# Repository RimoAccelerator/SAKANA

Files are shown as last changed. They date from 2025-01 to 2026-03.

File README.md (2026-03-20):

**非常重要提醒：20260320版本进行了重大更新，修正了在扫速控制和曲线显示方面的bug，包括固件和Controller，请务必更新。从旧版本更新过来的用户，请到Advance里，点击Reset，将预置的校正参数清除！**

**VERY Important Notice:** The 20260320 version includes major updates that fix bugs related to scan rate control and curve display. This update applies to both the firmware and the Controller—please make sure to update.

For users upgrading from older versions, go to **Advance**, click **Reset**, and clear the preset calibration parameters.

[中文](#cn) | [English](#en)

# SAKANA：年轻人第一台循环伏安的全面制造指南

SAKANA是一款基于树莓派Pico的电化学工作站，其中包含了所有软硬件信息。这篇介绍将从第一视角呈现SAKANA的开发和探索过程，以便读者透彻了解仪器的设计思想。

目录结构：

- **Hardware**
  
  Gerber_SAKANA_PCB.zip： PCB制板文件
  
  SAKANA_PCB.epro：PCB设计文件（基于立创EDA）
  
  Shell.zip：外壳模型，可进行3D打印

- **Sources**
  
  main.py：Pico上的Micropython文件

- **sources_SakanaController**
  
  上位机控制软件源代码，Releases中有编译后的可执行文件

鉴于绝大多数化学工作者都像我一样，没有接受过系统的电子工程教育，本文中会详细介绍电路的设计过程。如果你有此类基础，可直接跳转到**6. 建立连接**。

**1. 背景介绍**

   现代电化学工作站基于运算放大器（简称运放）进行设计，主要在20世纪70年代发展起来。早年文献中对电化学工作站的设计原则、特别是电路稳定性问题进行了诸多讨论，这些讨论对电路知识有较高的要求，有兴趣的读者可以自行查阅。近十多年来，得益于单片机技术的普及，使用以Arduino为代表的单片机控制从而低成本制造电化学工作站的案例不断见诸报道，以至于到了相当丰富的程度。甚至已经有学校将自制电化学工作站纳入了分析化学实验课程中（https://www.chem.uci.edu/~unicorn/243/labs/W2019Chem243Lab3.pdf）。

   

   本文的设计原型来自2016年Meloni的工作（J. Chem. Educ. 2016, 93, 7, 1320–1322）。Meloni报道了基于Arduino的电化学工作站设计，并给出了电路图和简易源代码。然而不幸的是，虽然Meloni文中呈现了良好的结果，但如果直接照搬它的设计，仔细考察，就会发现其实并不能用。接下来我们会展示这一电路的原理、以及本文的装置的设计和改进过程。

**2. Meloni原型机的原理**

   用于循环伏安的电化学工作站基于三电极系统。对三电极系统的理解是仪器分析课程的基本内容，本文不再赘述。一个合格的电化学工作站需要确保以下几点：

   a. 在参比电极(RE)上没有电流流过；

   b. 能精确控制工作电极（WE）相对于RE的电位，并且这一电位需要以最高几个Hz的频率变化；

   c. 能精确测量通过WE的电流，电流的量级在零点几到几百uA之间。

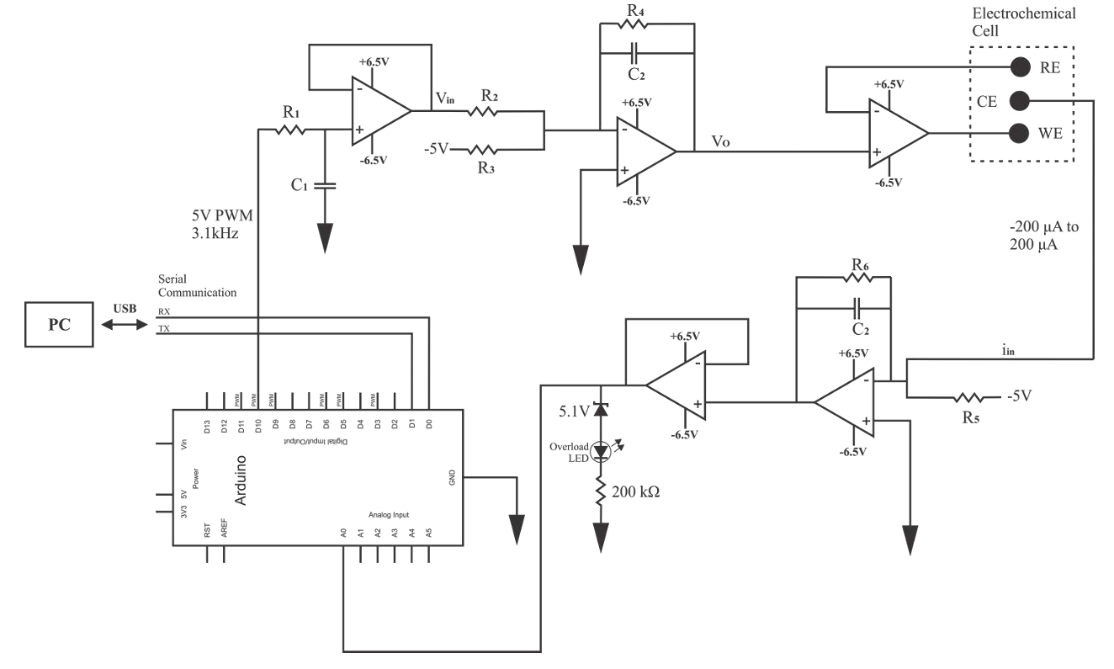
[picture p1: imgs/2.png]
   

a. 电压控制电路  

运放是现代电化学工作站的核心，要理解电压控制电路必须首先理解运放。

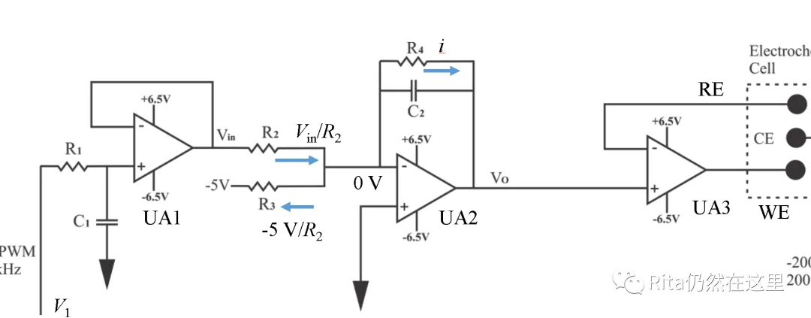
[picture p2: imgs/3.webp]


一个运放至少有5个引脚：2个电源引脚（图中正负6.5 V），一个同相输入端（图中+），一个反相输入端（图中-），一个输出端。当输出端与反相输入端通过电阻连接时，构成了负反馈电路；对于理想运放，输入端可视为无穷大的电阻，而一旦构成负反馈，则两个输入端电位相等且都没有电流流过。因此对于上图中左侧的运放，输出电压Vin始终等于同相输入端电位，这被称为跟随器，可对电路起到隔离作用。接下来为了解出第二个运放的输出电位Vo，可设通过R4的电流为i，则Vo = -iR4，可知运放对电流有放大作用，放大倍数取决于反馈电阻。由于通过反相输入端的电流为0，可知i = Vin / R2 - 5 V / R2，进而可求出Vo。通过控制Vin = V1，即可控制Vo；随后Vo接到UA3上，只要RE和CE放在电解池中，就再次构成负反馈，RE上的电压即等于V1。  

之所以要采用这样的设计，是由于多数单片机只能输出正电压，因此需要通过R3施加一个负电压偏置来将其转换为循环伏安所需要的电压范围。在Meloni原型机中，V1通过Arduino的PWM供给。PWM是通过让输出信号在0 V和（对于Arduino来说）5 V间快速切换产生方波的技术，假设占空比为a，则等效输出5 V * a的电压。为了将这种方波信号转换为循环伏安所需要的直流信号，Meloni原型机在R1和UA1之间对地接入电容C1，从而构成了RC滤波电路。RC滤波电路对电信号的阻抗随频率上升而快速增加，对于频率大于1/(2pi*RC)的信号，通过RC滤波器后衰减大于3 dB，这被称为截止频率。方波信号经过傅里叶展开后，可视为直流信号叠加一系列高频信号；理想上，当高频信号被充分滤除，就可以得到5 V * a的直流电压。随后经过UA1~UA3，最终反映到RE对地的电位上。

类似地，UA2上的C2同样与R4构成RC滤波器，从而尽可能滤除运放带来的噪声。

b. 电流采样电路

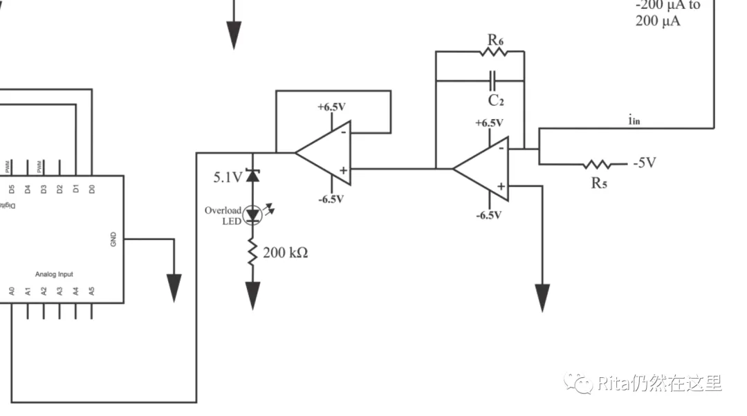
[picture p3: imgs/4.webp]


Meloni原型机中，电流采样电路接在CE上，通过R5施加5 V的偏置，接到运放上，通过R6负反馈，使得CE的电位恒为0。两者混合后的电流i被放大为电位iR6（恒为正，同样是由于单片机只能读取正电位），经过一个跟随器后进入Arduino的ADC引脚（Analog to Digital）从而被读取。读完上文后，相信读者已经会计算通过CE的电流与ADC读数的关系了。

你发现了什么不对了吗？

在Meloni原型机中，CE和WE的位置画反了。我们并不关心CE上的电位是多少，而必须控制WE和RE的电位差，因此必须将WE接在电流采集电路处，从而使得上面控制的RE相对于地的电位等同于WE相对于RE的电位的负值。  

总之，现在你已经理解了Meloni原型机的原理，接下来就开始实现吧。

**3. 材料清单**

- 

- | 名称               | 数量              | 链接                                                 | 备注      |
  | ---------------- | --------------- | -------------------------------------------------- | ------- |
  | 树莓派Pico          | 1               |                                                    |         |
  | MCP4725模块        | 1               | https://item.taobao.com/item.htm?&id=549632416001  |         |
  | ADS1115模块        | 1               | https://item.taobao.com/item.htm?&id=631122402654  |         |
  | INA219芯片         | 1               | https://item.taobao.com/item.htm?id=725297963549   |         |
  | 6 V输出DC/DC升压模块   | 1               | https://item.taobao.com/item.htm?id=666072862041   |         |
  | OP297运放          | 2               | https://item.taobao.com/item.htm?id=599390292581   |         |
  | 继电器模块            | 4（v1.0）或3（v2.0） | https://item.taobao.com/item.htm?&id=628701168992  |         |
  | CH340串口模块        | 1               | https://detail.tmall.com/item.htm?id=41323941056   |         |
  | GM12043AKCZ-R7   | 1               | https://item.szlcsc.com/8421183.html               | 仅v2.0需要 |
  | GM1206AUJZ-R7    | 1               | https://item.szlcsc.com/50919536.html              | 仅v2.0需要 |
  | 共模扼流圈ACM9070-272 | 1               | https://item.taobao.com/item.htm?id=711722477029   | 仅v2.0需要 |
  | 电容：10 uF         | 2               |                                                    |         |
  | 电容：2.2 uF        | 2               |                                                    | 仅v2.0需要 |
  | 电容：0.1 uF        | 10              |                                                    |         |
  | 电容：1 uF          | 3               |                                                    |         |
  | 电容：68 nF         | 1               |                                                    |         |
  | 电阻：4k7           | 4               |                                                    |         |
  | 电阻：10k           | 5               |                                                    |         |
  | 电阻：6k8           | 2               |                                                    |         |
  | 电阻：68k           | 1               |                                                    | 仅v1.0需要 |
  | 电阻：680k          | 1               |                                                    |         |
  | 电阻：1k            | 1               |                                                    |         |
  | 电阻：15k           | 2               |                                                    | 仅v2.0需要 |
  | GX16航空插座弯头       | 1               | https://item.taobao.com/item.htm?id=890416759846   | 仅v2.0需要 |
  | 屏蔽线母头GX16-4芯     | 1               | https://detail.tmall.com/item.htm?&id=691474825406 | 仅v2.0需要 |
  
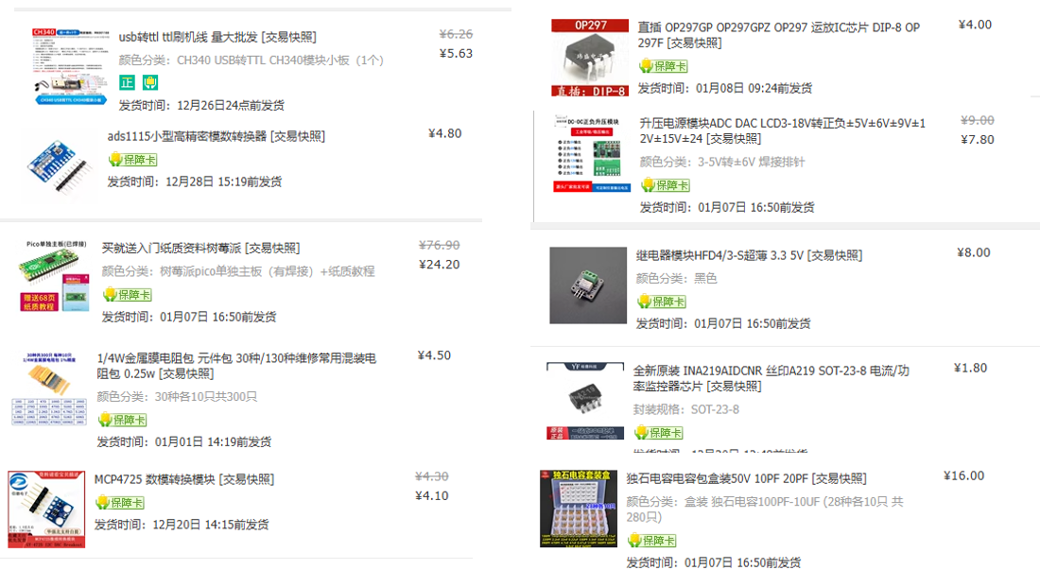
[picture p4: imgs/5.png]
  
  
  （没有任何淘宝店铺赞助本文）

Meloni使用了Arduino，而本文使用树莓派Pico。Pico的性能更为优异，而价格却更加低廉。值得注意的是Pico的输出电压是3.3 V（另有一个5 V引脚），因此基于输出5 V的Arduino的电路中元件取值要重新换算。  

**4. Meloni原型机的实现和失败，与第一版可工作的电路**  

Meloni已经给出了完整的电路图，将其实现是十分简单的事情，不再赘述。唯一值得一提的是，电路中需要使用负电压，仅使用Pico无法做到，本文中使用了升压电源模块得到正负6 V。正电压非常标准，而负电压实际大约为-5.5 V。它同样用于给运放供电。绝大多数运放的输出电压都位于两个电源引脚的电压之间，通常是一个较窄的范围（这将成为日后电阻选值的考量），选择轨到轨运放可以输出到接近供电电压的范围。

然而很快就会发现，这套电路的立足之本，即通过对PWM滤波以控制RE上的电位的做法完全不可行。一方面，即使经过滤波，电压仍然会不可避免地波动（纹波现象），而另一方面的问题则更加严重：

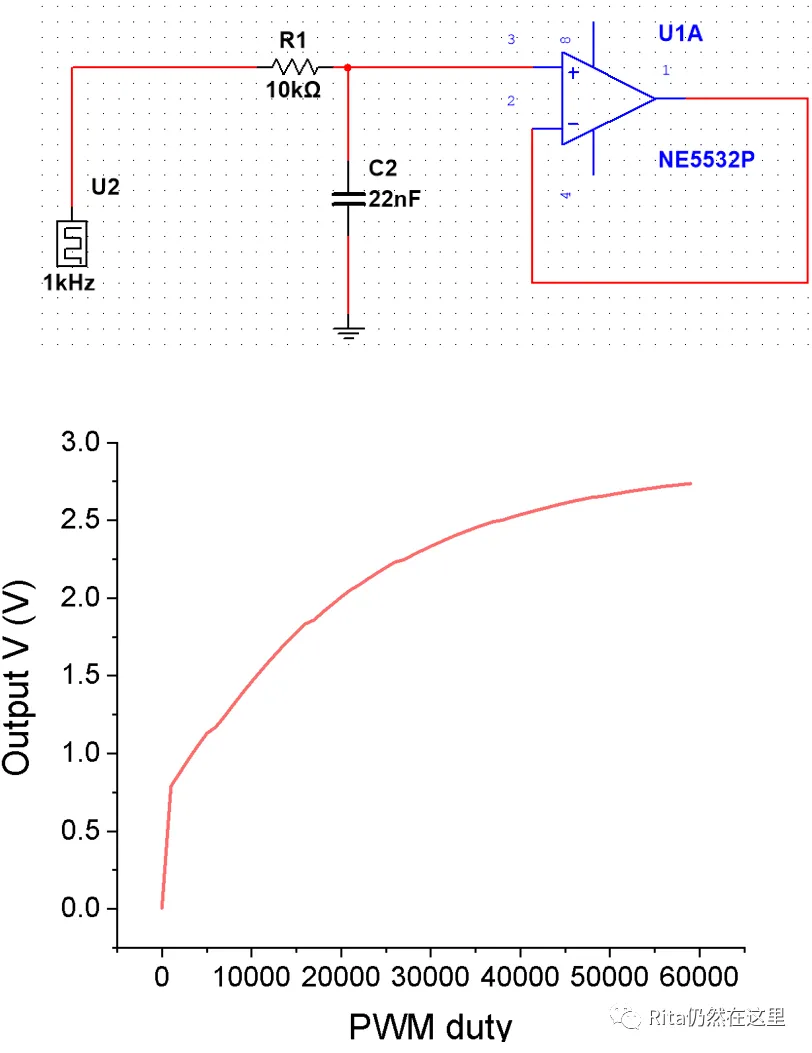
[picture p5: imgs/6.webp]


上图展示了PWM占空比与经过滤波得到的电压的关系。理想情况下，电压应随占空比呈现线性，但事实完全不同，呈现出一条十分不规则的曲线。这种情况下，通过PWM控制RE上的电压完全不可靠！  

幸运的是，由于现代电子工业高度发达，许多电路中的功能可以方便地找到模块，像搭积木一样处理。事实上，如果想输出可调的电压，并不需要手动设计电源电路，使用（3）中展示的MCP4725模块即可。它基于I2C协议和Pico连接，可以方便地使用Github上现成的库进行控制。经过实测，它可以精确、稳定地输出0 ~ 4.5 V的直流电压。

图片

使用MCP4725后，采用了如上电路以适配Pico的性能。在面包板上搭建好后，已经可以用于测定盐水中的赤血盐的CV：  

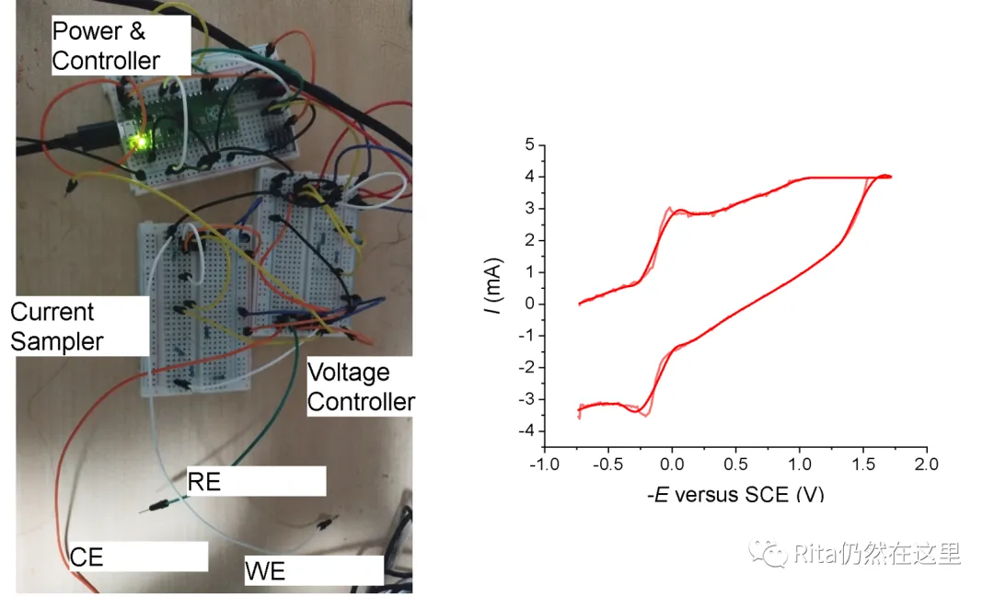
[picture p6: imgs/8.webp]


**5. 进一步改进：重做电流采样**  

上述电路如果作为教学实验，则已经可以了；但如果要用于实际测量，还存在诸多问题。其中最大的问题在于噪声。事实上，Pico ADC的噪声是一个世界性难题，许多人都受此困扰而难以找到解决方案。以下随机展示一个ADC面对直流电的测量结果，可见存在相当程度的不规则的跳变。这一噪声完全来自Pico自身的缺陷，无法被任何外部电路滤除。  

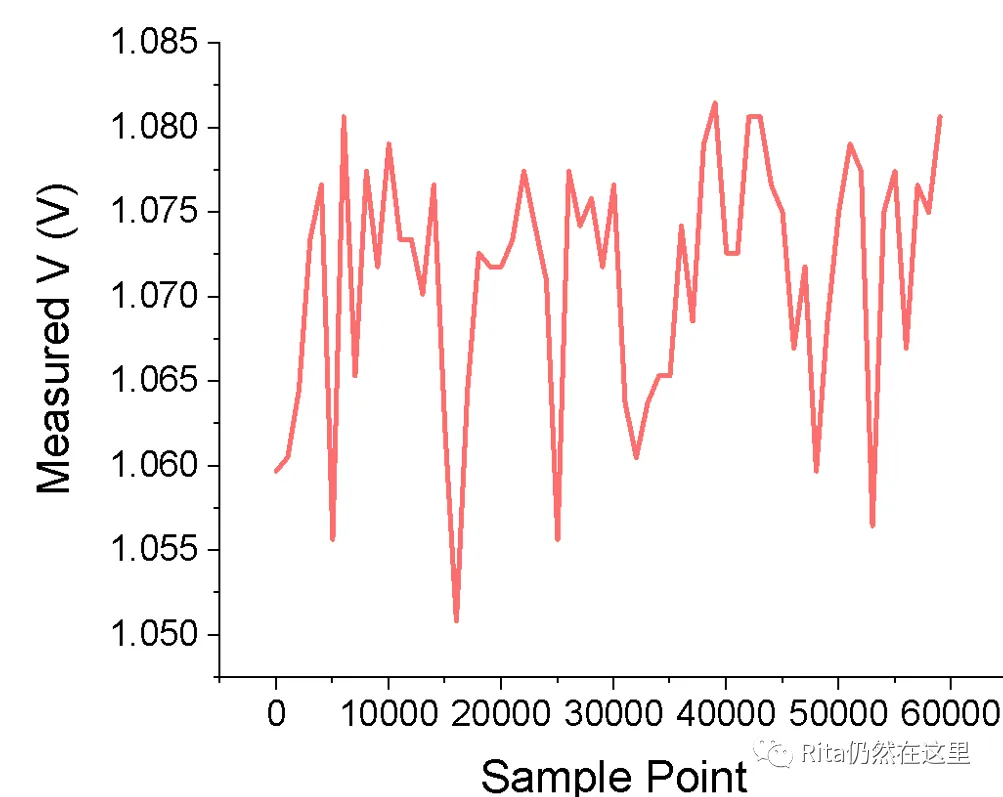
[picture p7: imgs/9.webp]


尽管Pico手册上给出了改进ADC的建议，但最终它们没能起效，因此接下来需要放弃Pico自带的ADC，采用其他模块。在这里，需要用到两个模块：ADS1115电压采集模块，以及INA219电流采集模块。两者都使用I2C协议，和MCP4725共用2根线进行通信。

事实证明，ADS1115的精度良好，可以非常平稳地测定接入的电压，并且可以测定不低于-0.5 V的负压。但问题在于采样频率，ADS1115每秒只能进行860次采样，无法满足CV测试在很短的时间内连续变化电压并进行采样的需求，如果硬上会造成死机。但它可以用于电路的校准：  

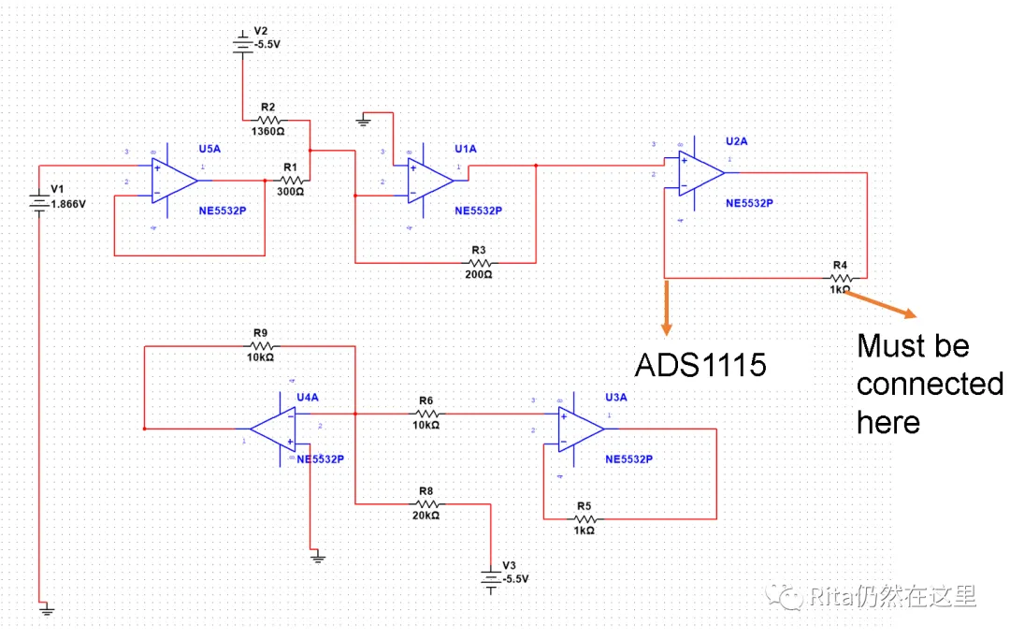
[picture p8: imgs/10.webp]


将RE和CE的接线端连起来（必须这样做，否则无法构成负反馈），用ADS1115测量RE处的电压，即可对仪器进行校准。  

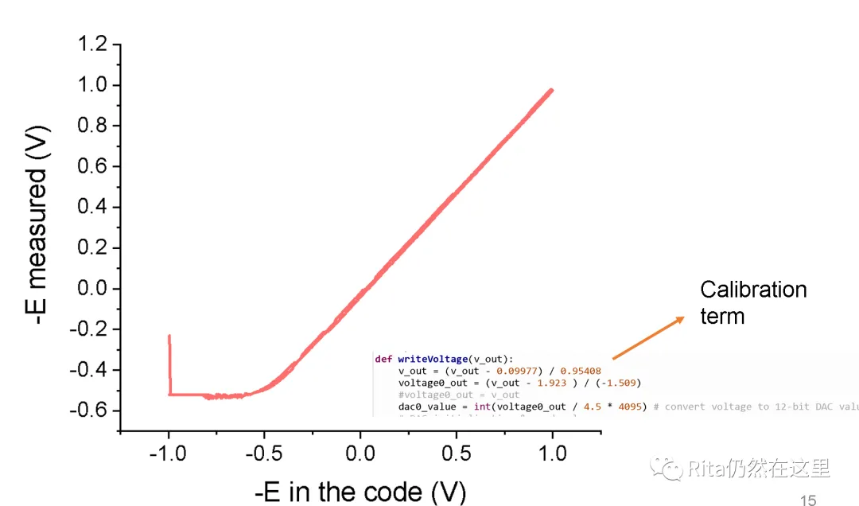
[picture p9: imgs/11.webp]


注意当电压小于-0.5 V时，ADS1115不再能正常工作，而且不仅自己不干活，还会干扰别人，导致RE上的电压异常，因此ADS1115只能用于校准，CV测量时必须同RE断开。

而接下来的INA219将成为电流采样的核心。它与ADC的思路不同，是直接测量电流。INA219本身是个集成电路，需要搭配外围电路使用，商业可得的INA219模块已经集成了一个0.1 Ohm的采样电阻，它通过测定采样电阻上的电压来给出电流，支持正负电流。量程可调，最小量程为400 mA，分辨率为12位，即400/(2^12)~0.1 mA。  

INA219的引入可以使得我们直接去掉电流采样电路冗杂的偏置电压设计，只要将流过WE的电流放大到合适的范围，让INA219采样即可。利用这种思路，在简单尝试后得到了十分积极的初步结果。其中黑线为原始信号，红线为经过平滑后的结果。

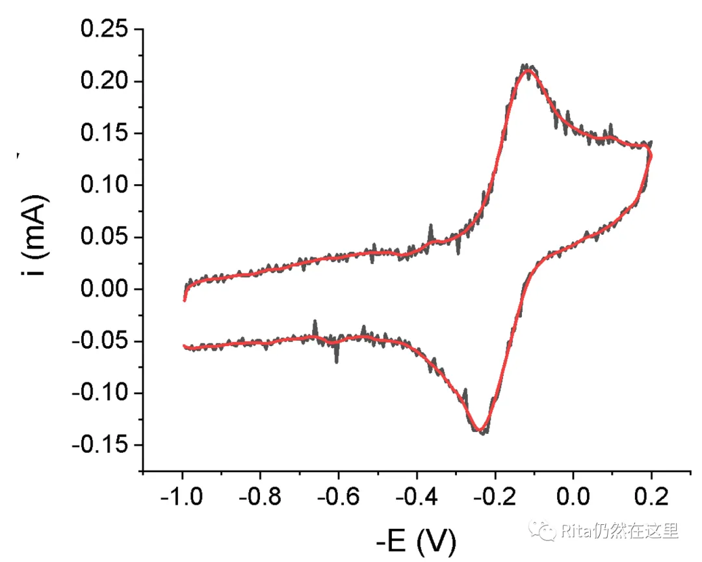
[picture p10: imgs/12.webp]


以下为SAKANA v1.0使用的电路：

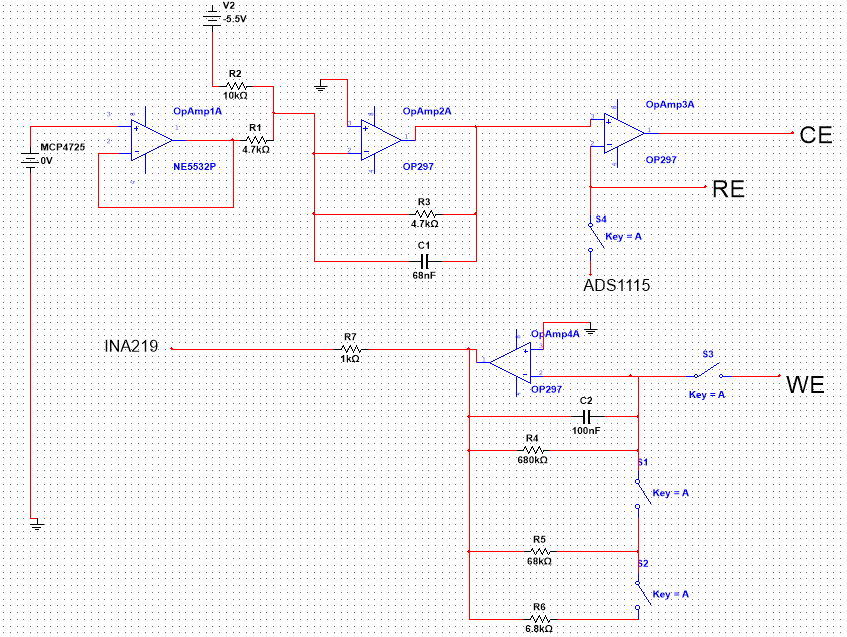
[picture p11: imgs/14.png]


在这一电路中，流过WE的电流i经过一个跨阻放大器，转化为iR的电压信号，其中R可在R4到R6之间选择。经过R7后，通过INA219的实际电流为iR/R7，测量这一电流信号即可换算为流过RE的电流。为了确保INA219的测量精度，iR/R7不能太小，需要在几个mA量级；同时iR又不能太大，必须落在运放能够可靠工作的电压范围内。由于CV波的电流从零点几到几百uA，跨越了3个数量级，采用两个继电器控制接入从6.8 k到680 k之间的电阻以改变量程。

OpAmp2和OpmAmp4的反馈回路上都并联有电容，起到增加运放稳定性和减少输出噪波的作用。借助示波器，可以清晰地看到C1对于确保RE上电压的稳定性有至关重要的作用。没有C1时，RE上的电压会以几百mV的幅度波动：

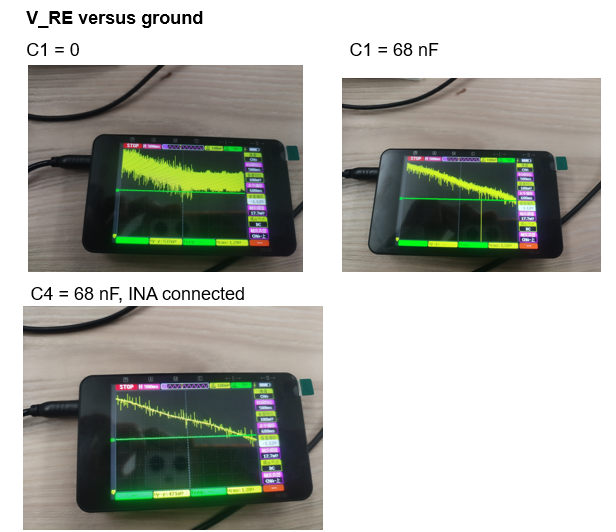
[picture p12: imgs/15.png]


C2同样可以显著抑制噪声。此处经过大量尝试，确定C2取值为100 nF，且不随接入的电阻而变化。较大的C2虽然可以进一步使得输出信号变得平滑，但由于滤除了太多快速变化的信号，导致波形畸变、以及更严重的是当改变设定的输出电压时需要相当长的时间才能达到稳定。

R7是一个1 kOhm的电阻。在设计初期，在R7处曾经使用过更小的电阻，寄希望于它能够使得流过INA219的电流尽可能大，以降低测定误差的影响。但不幸的是，较小的R7会导致测定曲线出现未曾预料的巨幅波动。以下是R7 = 100 Ohm的典型图形：

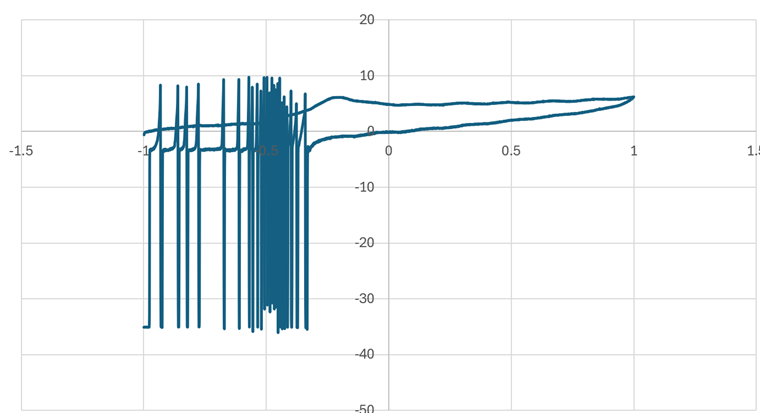
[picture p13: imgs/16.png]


经过大量尝试，确定R7为1 kOhm时，不会出现振荡现象。为了提高INA219的测量精度并与当前电阻的取值匹配，需要将它并联的采样电阻从0.1 Ohm改成10 Ohm。为了实现这一改动，既可以买来商品INA219模块，手动取下采样电阻后更换：

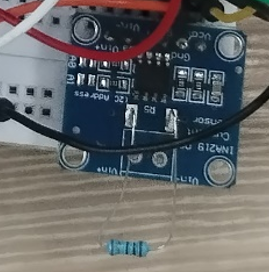
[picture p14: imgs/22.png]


也可以重新做一个自己的PCB，相关设计文件在Hardware里：

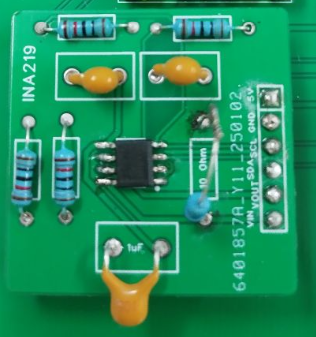
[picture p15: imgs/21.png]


**6. 建立连接**

在面包板上，将Pico与各模块连接，采用如下接线图（只标出模块之间的连接）：

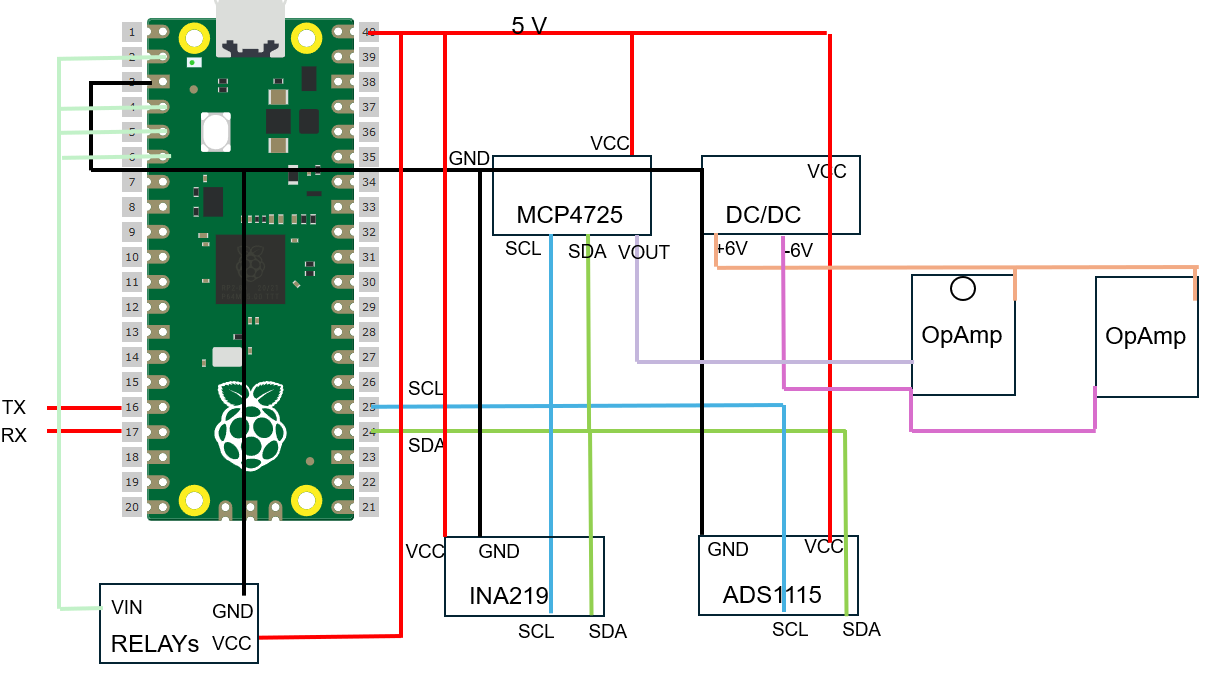
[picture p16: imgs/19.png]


其余部分连接可参照如下原理图：

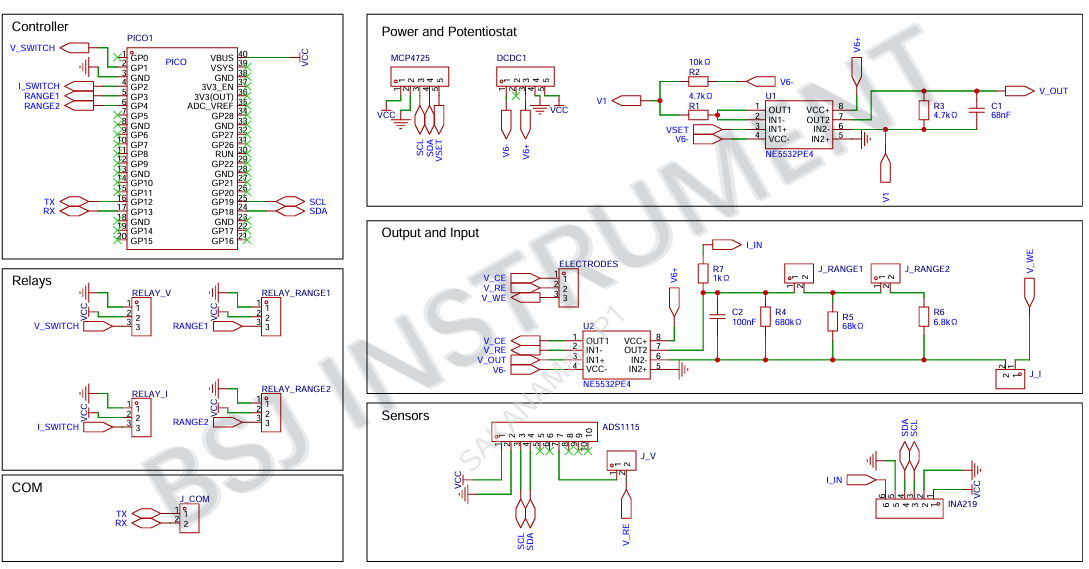
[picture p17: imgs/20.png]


在这里使用了4个继电器，其中2个用于控制量程，1个用于控制ADS1115只在希望进行电压校准时接到RE上（进行CV测定时必须断开，否则RE在负电压时不对），1个用于控制电流采集电路（只在进行CV测定时接上，否则电解池会被持续电解）。采用一个CH340串口模块实现与计算机的通信。连接完成后效果如下，可以使用配套软件非常方便地调试。

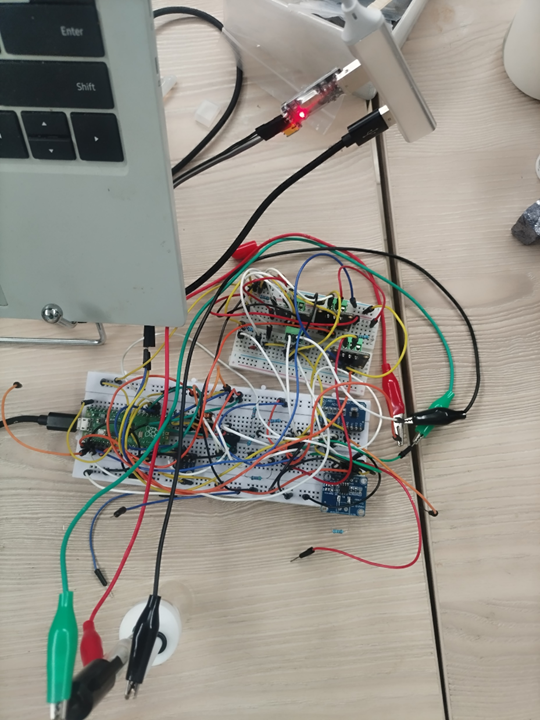
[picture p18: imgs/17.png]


**7. 配套软件**

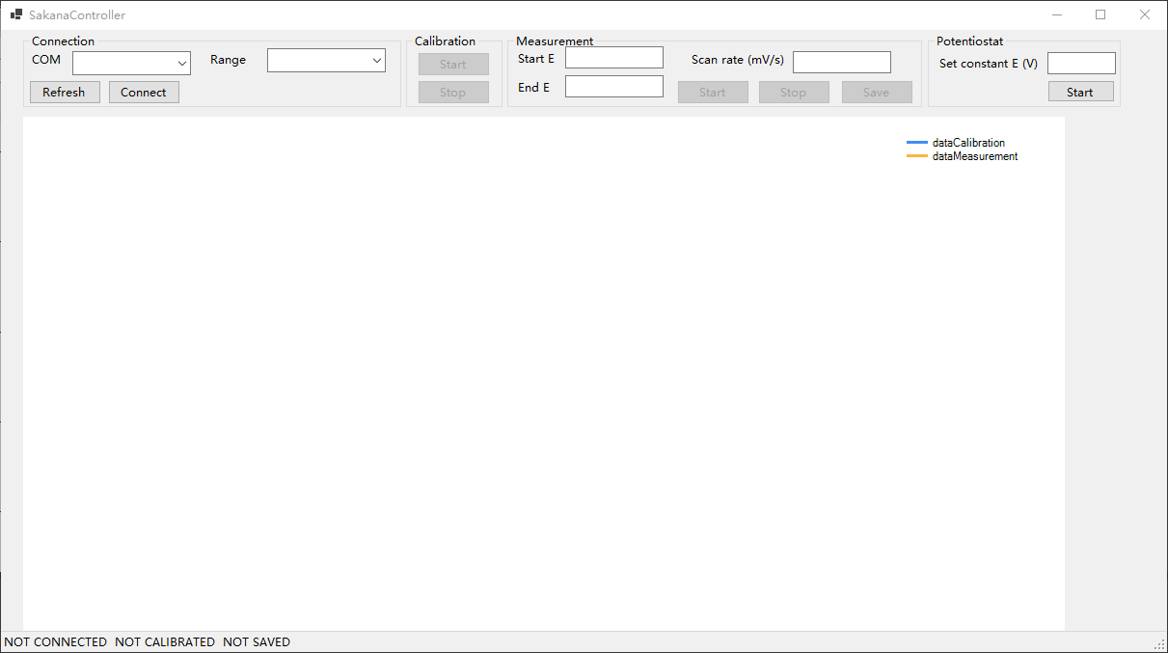
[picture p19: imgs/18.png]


SakanaController是针对Sakana的控制程序。在使用时，首先在Connection区域找到正确的串口并连接，然后在Calibration区域点击Start进行校准。正常情况下，应是一条斜向下的直线（第一个点处存在跳变，属于正常，不会带来任何影响）。此处的横坐标是MCP4725的输出电压，纵坐标为RE的电压，两者线性度非常好，可以在任何时候点击stop提前停止校准。校准完成后，将得到MCP4725电压与V_RE的相关系数，用于后续CV测试。

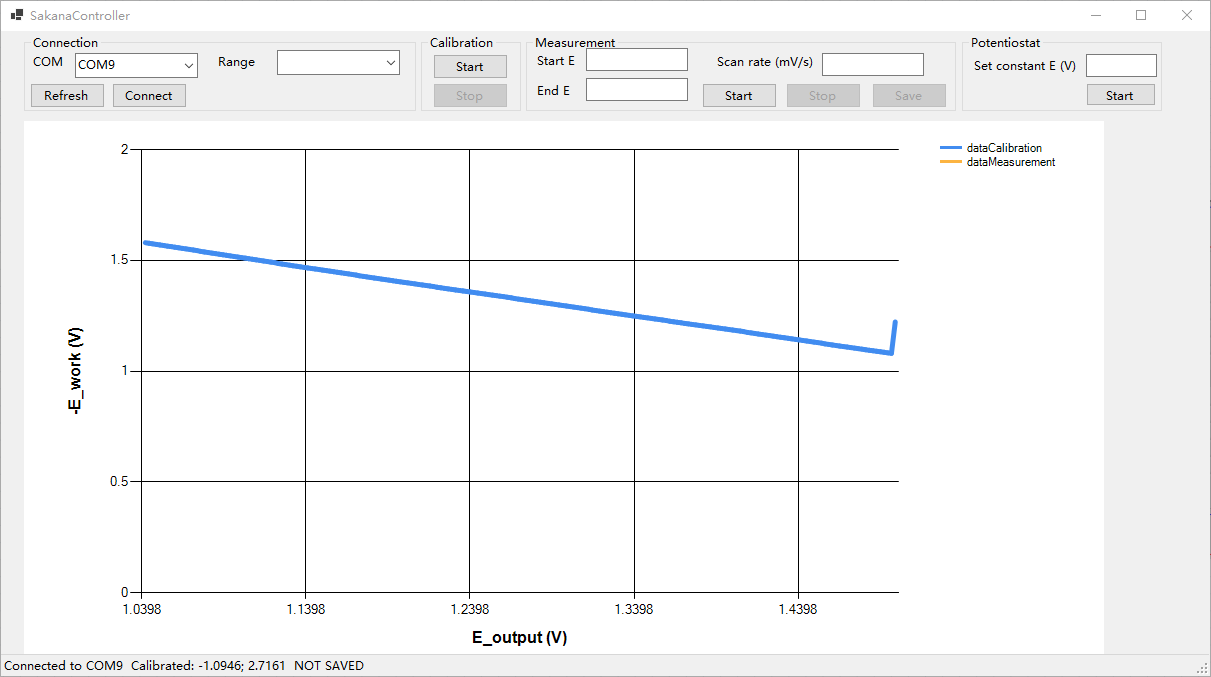
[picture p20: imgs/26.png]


在完成校准后，在Measurement区域设置测试参数，点击Start，测试就会开始，曲线实时更新。以下为部分结果案例。

*KCl中的黄血盐*

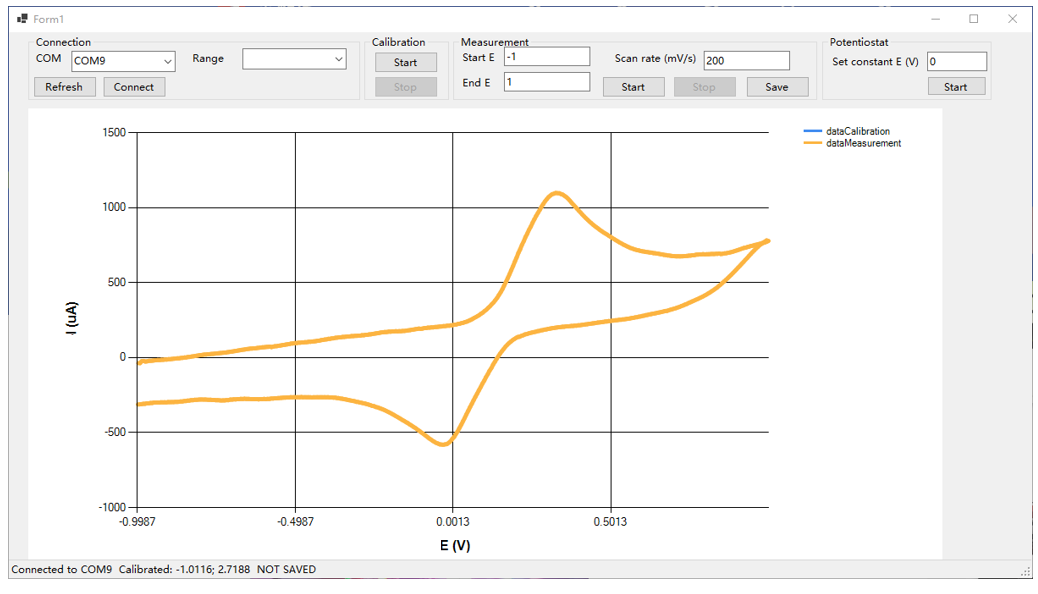
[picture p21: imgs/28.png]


*DCM中的二茂铁*

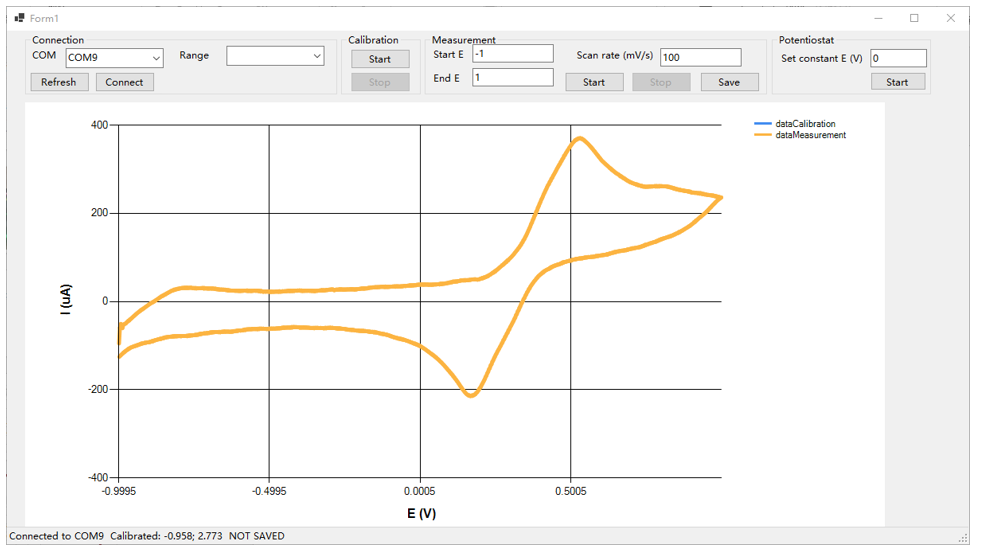
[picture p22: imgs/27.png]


测试完成后，点击Save，可以保存到纯文本文件。

1. 除了CV测量外，软件还有恒电位仪模式。完成校准后，在Potentiostat处输入期望的电压，点击Start，仪器就会让WE相对于RE的电位等于设置数值，可用于电解实验。对于焊接到PCB上的仪器，**电压范围可达正负2.5 V，误差在30 mV以内（典型值10 mV）**。

**8. 转移到PCB**  

在面包板上建立的电路虽然方便调试，但接触不良的现象非常严重，只要轻微触碰，仪器的表现就会改变，而焊接到PCB板上后就将得到非常可靠的成品。  

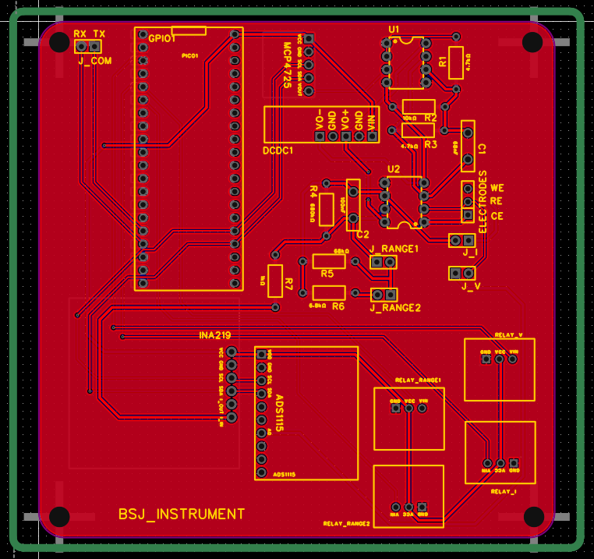
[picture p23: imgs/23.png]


绘制好原理图和PCB后，进行生产、焊接即可。

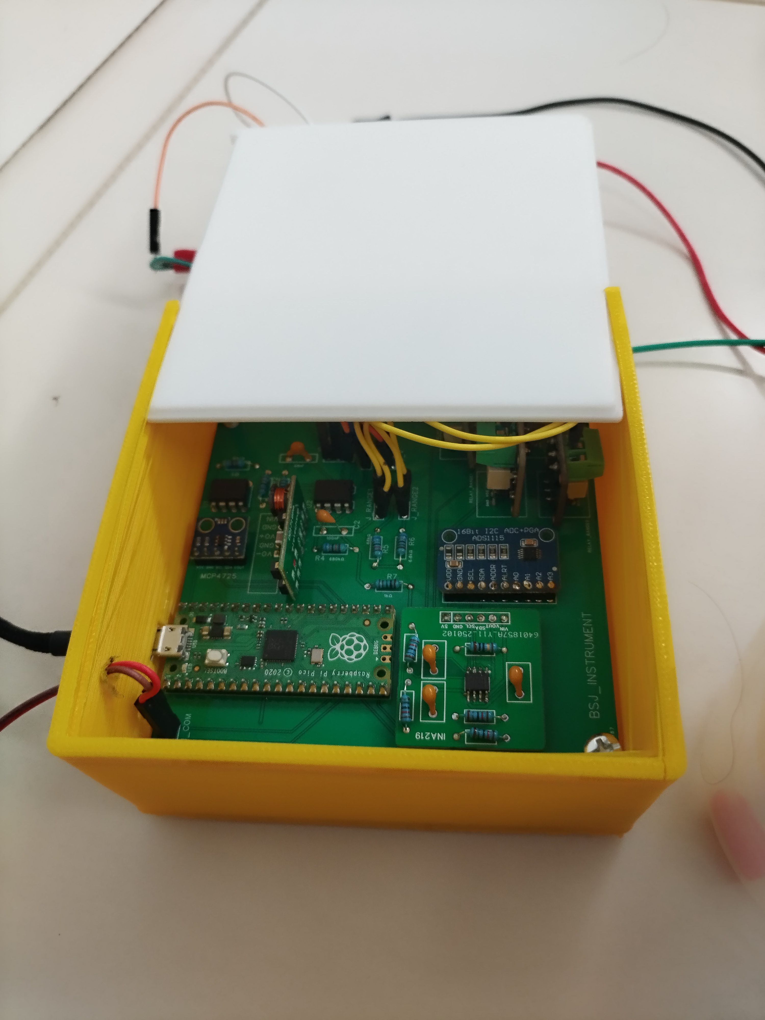
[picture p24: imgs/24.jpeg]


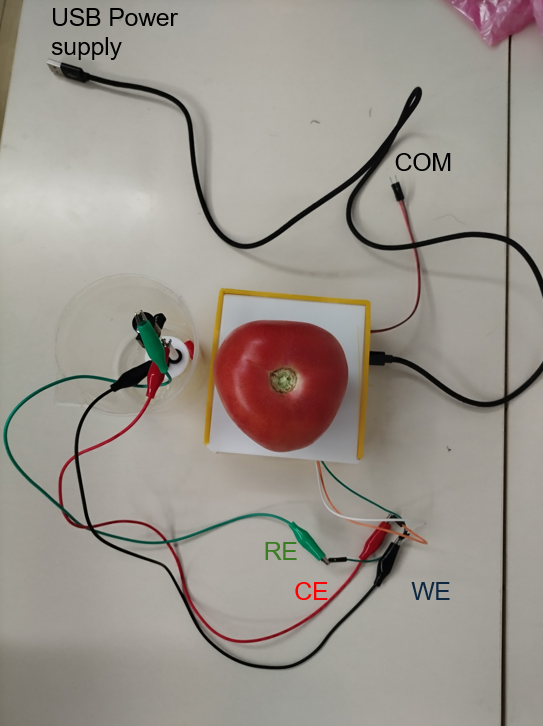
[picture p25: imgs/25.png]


至此，一个用于循环伏安的电化学工作站的v1.0版本就完成了。

SAKANA v1.0非常便于零基础人士制作，但有一个缺陷：所有的模拟供电都直接通过Pico或DCDC开关电源进行，这会带来非常严重的供电噪声。由于RE电压通过MCP4725输出与-6 V 开电源输出组合得到，这会直接在RE/WE直接引入100 mV左右的噪声，同时还叠加50 Hz工频干扰。这种噪声会导致电解池中很大的充放电电流，并且可能干扰测量得到的电化学行为。为此，我们需要进一步改进。

**9. SAKANA v2.0：进一步改善降低噪声**

为了进一步改善噪声问题，可以使用两个低噪声LDO，将LDO的稳压输出用于后续所有模拟电路的供电。来自共模半导体的GM1204和GM1206价格低廉，且可以在高达MHz的频率下保持极高的纹波抑制。在SAKANA v2.0中，来自DCDC的输出首先经过共模扼流圈L1，然后分别输入到两个LDO中，将+6/-6 V转换为+5/-5 V，用于运放、MCP4725、INA219、ADS1115的供电，并使用-5 V稳压输出与MCP4725输出一起形成RE的最终电位。

此外，由于在CV测试中，MCP4725实际输出的是台阶信号，在输出后加了一级RC滤波，使用Rf（10 kOhm）和C6（0.1 uF）构成时间常数约为1 ms的滤波器，一定程度上让台阶信号平滑化并减少过冲的影响。需要小心的是，此处滤波的时间常数不能太大：虽然CV需要尽可能平滑的三角波，但DPV则需要持续时间在几十个ms的尖锐脉冲信号。因此此处的取值需要权衡CV和DPV的需要。使用这一版电路，用示波器在PCB的RE接线口与GND处测量，噪声可以缩减到5 mV左右。

由于这两个LDO的封装很小，在焊接时需要格外小心，且需要使用热风枪。

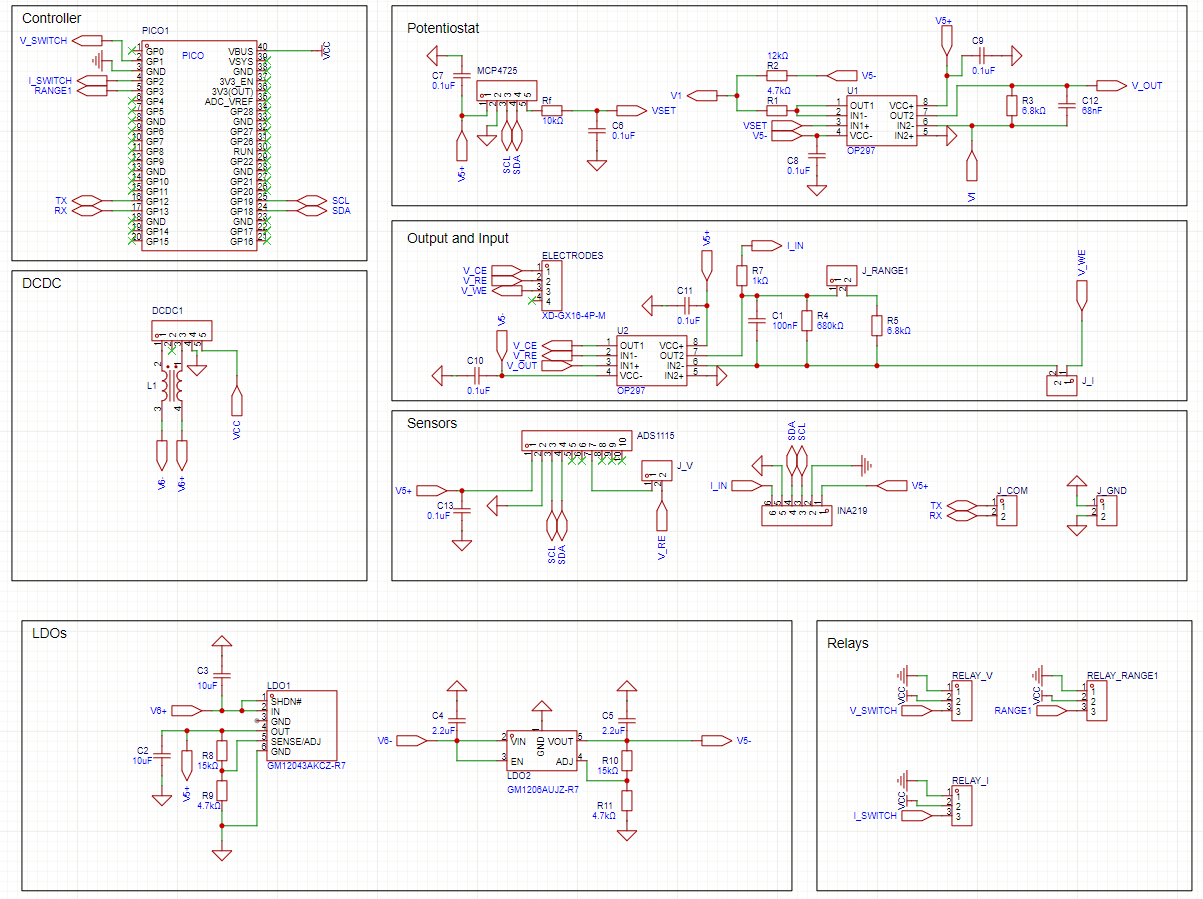
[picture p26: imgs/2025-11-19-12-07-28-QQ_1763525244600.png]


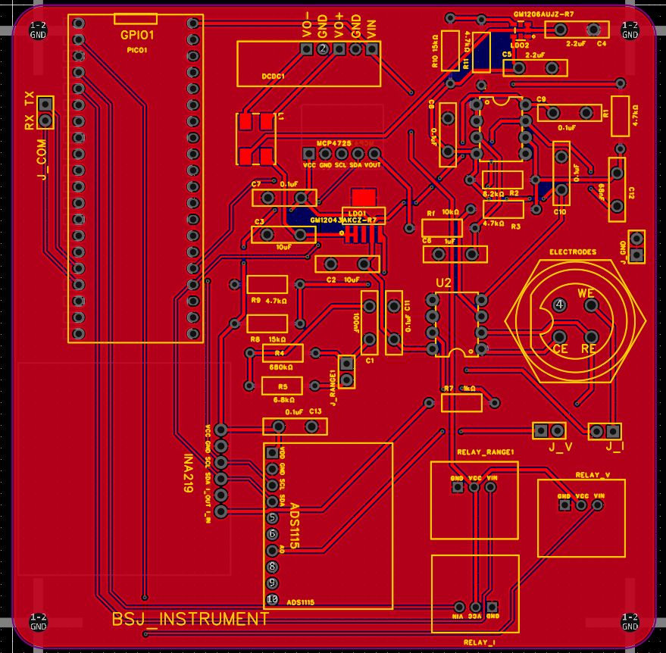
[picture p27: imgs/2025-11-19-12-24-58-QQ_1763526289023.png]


另一个重要的噪声源是伸出PCB的导线从环境中拾取的电磁波干扰，其中又以RE到电极的连接线最为重要。事实上，如果使用示波器对输出波形进行测量，就会很明显地感觉到环境干扰的重要影响：如果使用接线弹簧，噪声只有5 mV左右；而如果使用鳄鱼夹连接PCB与示波器，噪声会飙升到20 mV以上。这是由于任何导线环路在空气中都会时刻拾取空中的电磁波干扰。因此，即使RE/WE的电位在PCB上是准确且稳定的，一旦用普通导线接外界电解池，也会引入额外的噪声。为此，将原先使用3根导线连接电极的方法改成使用航空插头+屏蔽线；屏蔽线采用容易购得的4芯屏蔽线，只使用其中3根线，外层铜皮屏蔽层与金属航空插头连接，再在航空插头母座上用导线接地。屏蔽线另一端，手动焊上3个鳄鱼夹连接电极，要让暴露在屏蔽线外的导线尽可能短。使用这一方法，可以将最终输出的RE/GND电位噪声控制在10 mV以内。

在测试时需要注意，不能将示波器直接连接在RE/WE两端，否则会极大改变输出波形，导致剧烈震荡。为了测量这两者的电位，需要测的是RE/GND电位，也就是示波器一头接RE，另一头接PCB上的某个接地点。

此外，为了适配±5 V的供电，重新设计了各电阻的数值，使得支持的电位范围达到±2.8 V. 用于控制量程的继电器缩减到1个，分别对应百uA/1 uA级别的电流。

以下是SAKANA v2.0的实物照片。下位机固件使用v2.0版本，上位机控制软件完全相同。

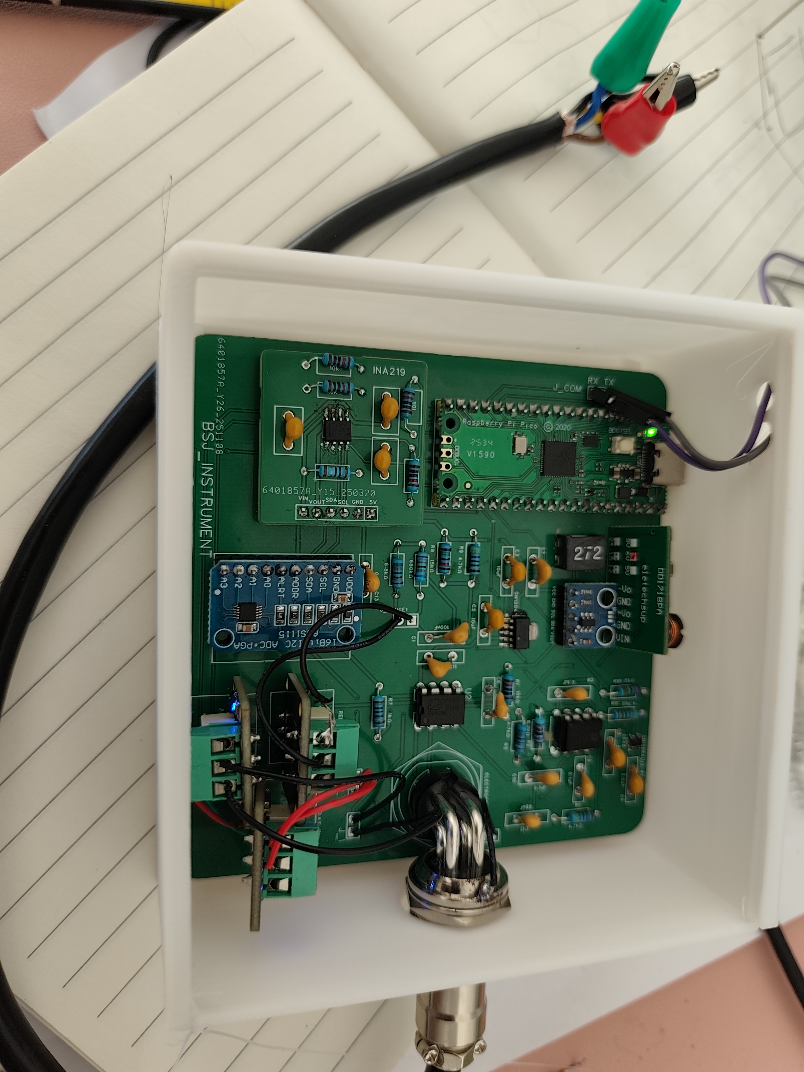
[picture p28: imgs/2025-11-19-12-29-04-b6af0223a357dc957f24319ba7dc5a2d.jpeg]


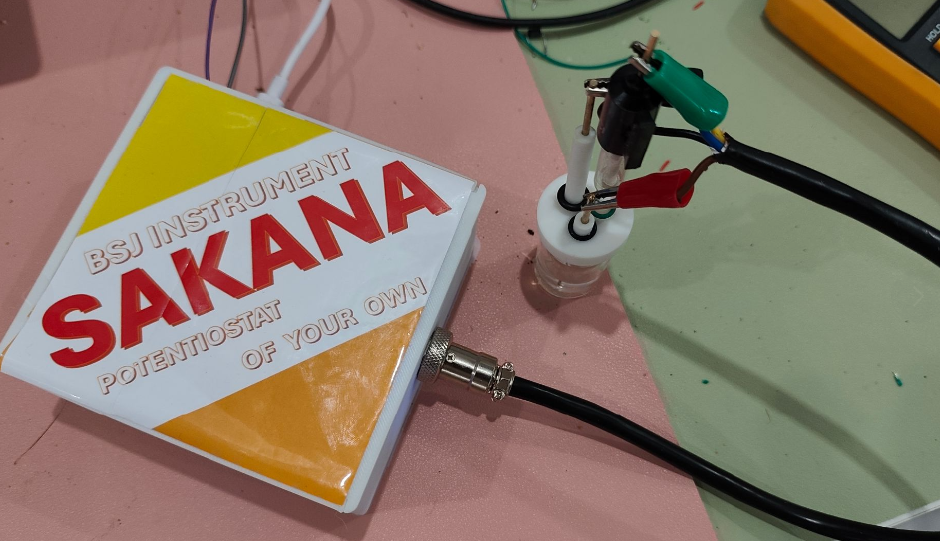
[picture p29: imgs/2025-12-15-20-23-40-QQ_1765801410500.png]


借助SAKANA Controller，可以测定CV、LSV、IT、DPV。以下是KCl水溶液中赤血盐的DPV测定示例：

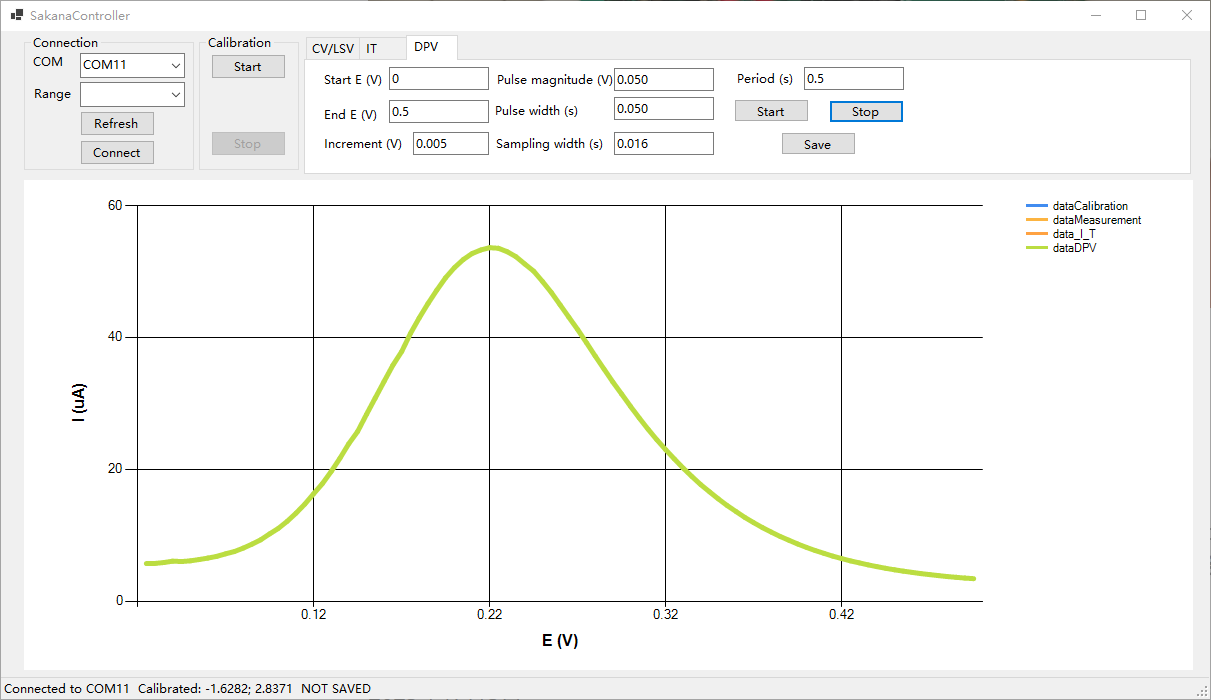
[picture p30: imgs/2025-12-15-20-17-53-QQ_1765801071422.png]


**关于**

这个项目的名称是SAKANA，发音与Cyclic相似。

非常鼓励读者将本文所介绍的内容用于自己的教学和研究中。凡引用本文者，必须标明出处。**凡进行发表、或基于本项目进行二次开发者，必须引用Github页面。禁止用于未经作者同意的商业用途。**

*BSJ INSTRUMENT 泊州仪器*

2025年1月15日

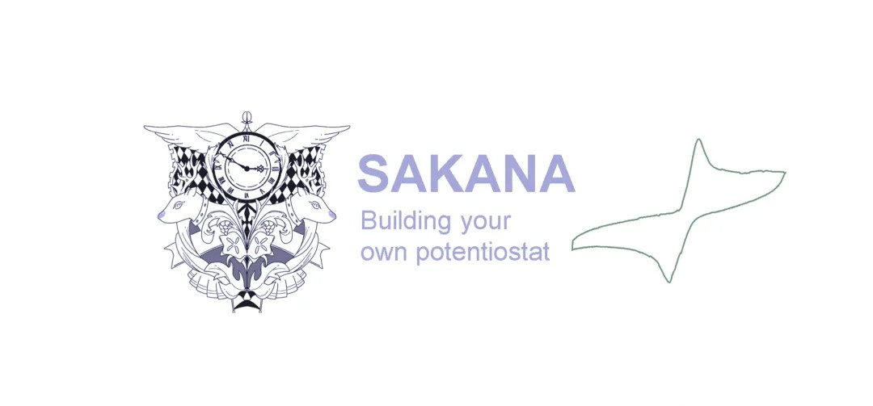
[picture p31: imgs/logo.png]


本项目使用了如下Github仓库中的成果：

[chrisb2/pyb_ina219: This library for MicroPython makes it easy to leverage the complex functionality of the Texas Instruments INA219 sensor to measure voltage, current and power.](https://github.com/chrisb2/pyb_ina219)

[robert-hh/ads1x15: Micropython driver for ADS1115 and ADS1015](https://github.com/robert-hh/ads1x15)

---

# SAKANA: The First Comprehensive Guide to Building a Cyclic Voltammetry Instrument

This is an electrochemical workstation (potentiostat) based on the Raspberry Pi Pico, containing all hardware and software information. This introduction presents the development and exploration process of SAKANA from a first-person perspective, allowing readers to thoroughly understand the design philosophy of the instrument.

### Directory Structure

- **Hardware**
  
  - `Gerber_SAKANA_PCB.zip`: PCB fabrication files (Gerber).
  - `SAKANA_PCB.epro`: PCB design file (based on EasyEDA).
  - `Shell.zip`: Shell model, ready for 3D printing.

- **Sources**
  
  - `main.py`: Micropython file for the Pico.

- **sources_SakanaController**
  
  - Source code for the PC host software. Compiled executables can be found in Releases.

---

Given that most chemists, like me, have not received systematic education in electronic engineering, this article will detail the circuit design process. If you already have this background, you can skip directly to **6. Connection**.

**1. Background**

Modern electrochemical workstations are designed based on operational amplifiers (Op-Amps) and were primarily developed in the 1970s. Early literature discussed the design principles of potentiostats, especially circuit stability issues, extensively. These discussions require a high level of circuit knowledge, and interested readers can look them up. Over the past decade, thanks to the popularity of microcontroller technology, low-cost potentiostats controlled by microcontrollers like Arduino have been reported frequently. It has become so common that some schools have even incorporated DIY potentiostats into their analytical chemistry laboratory courses (https://www.chem.uci.edu/~unicorn/243/labs/W2019Chem243Lab3.pdf).



The design prototype of this project comes from Meloni's work in 2016 (*J. Chem. Educ.* 2016, 93, 7, 1320–1322). Meloni reported an Arduino-based potentiostat design and provided circuit diagrams and simple source code. Unfortunately, although Meloni presented good results in the paper, a careful examination reveals that simply copying the design does not work. Next, we will demonstrate the principles of that circuit, as well as the design and improvement process of the device presented here.

**2. Principle of the Meloni Prototype**

Electrochemical workstations used for cyclic voltammetry (CV) are based on a three-electrode system. Understanding the three-electrode system is basic content in instrumental analysis courses, so it will not be repeated here. A qualified potentiostat needs to ensure the following:

a. No current flows through the Reference Electrode (RE).

b. It can precisely control the potential of the Working Electrode (WE) relative to the RE, and this potential needs to change at a frequency of up to several Hz.

c. It can precisely measure the current passing through the WE, with magnitudes ranging from fractions of a microampere to several hundred microamperes.



**a. Voltage Control Circuit**

The Op-Amp is the core of modern electrochemical workstations. To understand the voltage control circuit, one must first understand the Op-Amp.

图片

An Op-Amp has at least 5 pins: 2 power pins (+/- 6.5 V in the figure), a non-inverting input (+), an inverting input (-), and an output. When the output is connected to the inverting input via a resistor, a negative feedback circuit is formed. For an ideal Op-Amp, the input terminals have infinite resistance. Once negative feedback is established, the potentials of the two input terminals are equal, and no current flows through them. Therefore, for the Op-Amp on the left in the figure above, the output voltage Vin always equals the non-inverting input potential. This is called a voltage follower and provides circuit isolation. 

To solve for the output potential Vo of the second Op-Amp, let the current through R4 be *i*. Then Vo = -iR4. This shows the Op-Amp amplifies current, with the gain depending on the feedback resistor. Since the current through the inverting input is 0, we know `i = Vin / R2 - 5 V / R2`, from which Vo can be calculated. By controlling Vin = V1, Vo can be controlled. Vo is then connected to UA3. As long as RE and CE are placed in the electrolytic cell, negative feedback is formed again, and the voltage on RE equals V1.

This design is adopted because most microcontrollers can only output positive voltages. Therefore, a negative voltage bias is applied via R3 to convert it to the voltage range required for cyclic voltammetry. In the Meloni prototype, V1 is supplied by the Arduino's PWM. PWM creates a square wave by rapidly switching the output signal between 0 V and 5 V (for Arduino). Assuming a duty cycle of *a*, the equivalent output voltage is `5 V * a`. To convert this square wave signal into the DC signal required for CV, the Meloni prototype connects capacitor C1 to ground between R1 and UA1, forming an RC filter circuit. An RC filter's impedance to electrical signals increases rapidly with frequency. For signals with a frequency greater than `1/(2pi*RC)`, the attenuation after passing through the RC filter is greater than 3 dB; this is called the cutoff frequency. A square wave signal can be viewed as a DC signal superimposed with a series of high-frequency signals after Fourier expansion. Ideally, when the high-frequency signals are fully filtered out, a DC voltage of `5 V * a` is obtained. This is then passed through UA1~UA3 and finally reflected in the potential of RE relative to the ground.

Similarly, C2 on UA2 forms an RC filter with R4 to filter out noise from the Op-Amp as much as possible.

**b. Current Sampling Circuit**

图片

In the Meloni prototype, the current sampling circuit is connected to the CE. A 5 V bias is applied via R5, connected to the Op-Amp, and negative feedback is provided via R6, keeping the CE potential constant at 0. The mixed current *i* is amplified to a potential *iR6* (always positive, again because the microcontroller can only read positive potentials). After passing through a follower, it enters the Arduino's ADC (Analog to Digital) pin to be read. After reading the above, I believe readers can calculate the relationship between the current through CE and the ADC reading.

**Did you notice something wrong?**

In the Meloni prototype, the positions of CE and WE are reversed. We do not care what the potential on the CE is, but we must control the potential difference between WE and RE. Therefore, the WE must be connected to the current collection circuit so that the potential of RE relative to the ground controlled above is equal to the negative value of the potential of WE relative to RE.

Anyway, now that you understand the principle of the Meloni prototype, let's start building it.

**3. Bill of Materials (BOM)**

- 1 * Raspberry Pi Pico
- 1 * MCP4725 Module
- 1 * ADS1115 Module
- 1 * INA219 Chip
- 1 * 6 V Output DC/DC Boost Module
- 2 * OP297 Op-Amp
- 4 * Relay Modules
- 1 * CH340 Serial Module
- Various capacitors and resistors

Total cost is around 100 RMB.

| Name                            | Qty                  | Link (Taobao/LCSC)                                         | Notes     |
|:------------------------------- |:-------------------- |:---------------------------------------------------------- |:--------- |
| Raspberry Pi Pico               | 1                    |                                                            |           |
| MCP4725 Module                  | 1                    | [Link](https://item.taobao.com/item.htm?&id=549632416001)  |           |
| ADS1115 Module                  | 1                    | [Link](https://item.taobao.com/item.htm?&id=631122402654)  |           |
| INA219 Chip                     | 1                    | [Link](https://item.taobao.com/item.htm?id=725297963549)   |           |
| 6V Output DC/DC Boost Module    | 1                    | [Link](https://item.taobao.com/item.htm?id=666072862041)   |           |
| OP297 Op-Amp                    | 2                    | [Link](https://item.taobao.com/item.htm?id=599390292581)   |           |
| Relay Module                    | 4 (v1.0) or 3 (v2.0) | [Link](https://item.taobao.com/item.htm?&id=628701168992)  |           |
| CH340 Serial Module             | 1                    | [Link](https://detail.tmall.com/item.htm?id=41323941056)   |           |
| GM12043AKCZ-R7                  | 1                    | [Link](https://item.szlcsc.com/8421183.html)               | v2.0 only |
| GM1206AUJZ-R7                   | 1                    | [Link](https://item.szlcsc.com/50919536.html)              | v2.0 only |
| Common Mode Choke ACM9070-272   | 1                    | [Link](https://item.taobao.com/item.htm?id=711722477029)   | v2.0 only |
| Cap: 10 uF                      | 2                    |                                                            |           |
| Cap: 2.2 uF                     | 2                    |                                                            | v2.0 only |
| Cap: 0.1 uF                     | 10                   |                                                            |           |
| Cap: 1 uF                       | 3                    |                                                            |           |
| Cap: 68 nF                      | 1                    |                                                            |           |
| Resistor: 4k7                   | 4                    |                                                            |           |
| Resistor: 10k                   | 5                    |                                                            |           |
| Resistor: 6k8                   | 2                    |                                                            |           |
| Resistor: 68k                   | 1                    |                                                            | v1.0 only |
| Resistor: 680k                  | 1                    |                                                            |           |
| Resistor: 1k                    | 1                    |                                                            |           |
| Resistor: 15k                   | 2                    |                                                            | v2.0 only |
| GX16 Aviation Socket (Elbow)    | 1                    | [Link](https://item.taobao.com/item.htm?id=890416759846)   | v2.0 only |
| Shielded Wire Female GX16-4 Pin | 1                    | [Link](https://detail.tmall.com/item.htm?&id=691474825406) | v2.0 only |



*(No Taobao shop sponsored this article)*

Meloni used an Arduino, while this article uses a Raspberry Pi Pico. The Pico has superior performance and is cheaper. Note that the Pico's output voltage is 3.3 V (there is also a 5 V pin), so component values in circuits based on the 5 V output Arduino need to be recalculated.

**4. Implementation and Failure of the Meloni Prototype, and the First Working Circuit**

Meloni provided the complete circuit diagram, so implementing it is very simple and won't be repeated here. The only thing worth mentioning is that the circuit requires a negative voltage, which the Pico alone cannot provide. In this article, a boost power module is used to obtain +/- 6 V. The positive voltage is very standard, while the negative voltage is actually about -5.5 V. It is also used to power the Op-Amps. The output voltage of most Op-Amps lies between the voltages of the two power pins, usually a narrower range (this will be a consideration for resistor selection later). Choosing a Rail-to-Rail Op-Amp allows output closer to the supply voltage range.

However, you will soon discover that the core principle of this circuit—controlling the potential on the RE by filtering PWM—is completely unfeasible. On the one hand, even after filtering, the voltage will inevitably fluctuate (ripple). On the other hand, the problem is even more serious:

图片

The figure above shows the relationship between the PWM duty cycle and the voltage obtained after filtering. Ideally, the voltage should be linear with the duty cycle, but the reality is completely different, showing a very irregular curve. In this case, controlling the voltage on the RE via PWM is completely unreliable!

Fortunately, the modern electronics industry is highly developed, and many circuit functions can be easily found as modules, handled like building blocks. In fact, if you want to output an adjustable voltage, you don't need to design a power circuit manually; you can use the MCP4725 module shown in (3). It connects to the Pico based on the I2C protocol and can be easily controlled using existing libraries on Github. Tests show that it can precisely and stably output a DC voltage of 0 ~ 4.5 V.

图片

After using the MCP4725, the circuit above was adopted to adapt to the Pico's performance. After building it on a breadboard, it could already be used to determine the CV of ferricyanide in salt water:

图片

**5. Further Improvement: Redoing Current Sampling**

The above circuit is fine if used as a teaching experiment; however, if it is to be used for actual measurement, there are still many problems. The biggest problem lies in noise. In fact, the noise of the Pico ADC is a global problem, and many people are troubled by it and struggle to find a solution. Below is a random display of an ADC measurement result for DC current, showing a considerable degree of irregular jumping. This noise comes entirely from the Pico's own defects and cannot be filtered out by any external circuit.

图片

Although the Pico manual gives suggestions for improving the ADC, they ultimately failed to work. Therefore, we need to abandon the Pico's built-in ADC and use other modules. Here, two modules are needed: the ADS1115 voltage acquisition module and the INA219 current acquisition module. Both use the I2C protocol and share 2 wires for communication with the MCP4725.

It turns out that the accuracy of the ADS1115 is good; it can measure the connected voltage very smoothly and can measure negative voltages not lower than -0.5 V. But the problem lies in the sampling frequency. The ADS1115 can only sample 860 times per second, which cannot meet the needs of CV testing to continuously change the voltage and sample in a very short time. If forced, it will cause a crash. However, it can be used for circuit calibration:

图片

Connect the RE and CE terminals together (this must be done, otherwise negative feedback cannot be formed), and use the ADS1115 to measure the voltage at the RE to calibrate the instrument.

图片

Note that when the voltage is less than -0.5 V, the ADS1115 can no longer work properly. Moreover, it not only stops working itself but also interferes with others, causing abnormalities in the voltage on the RE. Therefore, the ADS1115 can only be used for calibration and must be disconnected from the RE during CV measurement.

The INA219 will become the core of current sampling. It differs from the ADC approach by measuring current directly. The INA219 itself is an integrated circuit that needs to be used with peripheral circuits. Commercially available INA219 modules already integrate a 0.1 Ohm sampling resistor. It gives the current by measuring the voltage across the sampling resistor and supports positive and negative currents. The range is adjustable, with a minimum range of 400 mA and a resolution of 12 bits, i.e., `400/(2^12) ~ 0.1 mA`.

The introduction of the INA219 allows us to directly remove the cumbersome bias voltage design of the current sampling circuit. We only need to amplify the current flowing through the WE to a suitable range and let the INA219 sample it. Using this idea, very positive preliminary results were obtained after simple attempts. The black line is the original signal, and the red line is the smoothed result.

图片

The following is the circuit used by SAKANA v1.0:



In this circuit, the current *i* flowing through the WE passes through a transimpedance amplifier and is converted into a voltage signal *iR*, where R can be selected between R4 and R6. After passing through R7, the actual current through the INA219 is *iR/R7*. Measuring this current signal can be converted to the current flowing through the RE. To ensure the measurement accuracy of the INA219, *iR/R7* cannot be too small and needs to be in the order of a few mA; at the same time, *iR* cannot be too large and must fall within the voltage range where the Op-Amp can work reliably. Since the current of the CV wave spans 3 orders of magnitude from fractions of a microampere to several hundred microamperes, two relays are used to control the access to resistors between 6.8 k and 680 k to change the range.

Capacitors are connected in parallel to the feedback loops of OpAmp2 and OpAmp4 to increase Op-Amp stability and reduce output noise. With the help of an oscilloscope, it can be clearly seen that C1 plays a vital role in ensuring the stability of the voltage on the RE. Without C1, the voltage on the RE would fluctuate by hundreds of mV:



C2 can also significantly suppress noise. After extensive attempts, it was determined that C2 should be 100 nF and does not change with the accessed resistor. Although a larger C2 can further smooth the output signal, it filters out too many rapidly changing signals, causing waveform distortion. More seriously, it takes a long time to stabilize when the set output voltage changes.

R7 is a 1 kOhm resistor. In the early stages of design, a smaller resistor was used at R7, hoping to maximize the current flowing through the INA219 to reduce the impact of measurement errors. Unfortunately, a smaller R7 causes huge fluctuations in the measurement curve that were not expected. The following is a typical graph for R7 = 100 Ohm:



After many attempts, it was determined that oscillation does not occur when R7 is 1 kOhm. To improve the measurement accuracy of the INA219 and match the current resistor value, the parallel sampling resistor needs to be changed from 0.1 Ohm to 10 Ohm. To achieve this change, you can buy a commercial INA219 module, manually remove the sampling resistor, and replace it:



You can also make your own PCB. The relevant design files are in the Hardware folder:



**6. Connection**

On the breadboard, connect the Pico to various modules using the following wiring diagram (only showing connections between modules):



For the rest of the connections, refer to the schematic diagram below:



Here, 4 relays are used. 2 are used to control the range, 1 is used to control the ADS1115 to connect to the RE only when voltage calibration is desired (it must be disconnected during CV measurement, otherwise the RE is incorrect at negative voltages), and 1 is used to control the current collection circuit (connected only during CV measurement, otherwise the electrolytic cell will be continuously electrolyzed). A CH340 serial module is used to communicate with the computer. The effect after connection is as follows, and it can be debugged very conveniently using the supporting software.



**7. Supporting Software**



SakanaController is the control program for Sakana. When using it, first find the correct serial port in the Connection area and connect. Then click Start in the Calibration area to calibrate. Normally, it should be a straight line sloping downwards (a jump at the first point is normal and will not have any impact). Here, the abscissa is the output voltage of the MCP4725, and the ordinate is the voltage of the RE. The linearity between the two is very good. You can click stop at any time to stop calibration early. After calibration is complete, the correlation coefficient between MCP4725 voltage and V_RE will be obtained for subsequent CV testing.



After calibration is complete, set the test parameters in the Measurement area and click Start. The test will begin, and the curve will update in real-time. The following are some result examples.

*Ferricyanide in KCl*



*Ferrocene in DCM*



After the test is complete, click Save to save to a plain text file.

1. In addition to CV measurement, the software also has a Potentiostat mode. After completing calibration, input the desired voltage in Potentiostat and click Start. The instrument will set the potential of WE relative to RE equal to the set value, which can be used for electrolysis experiments. For instruments soldered onto the PCB, **the voltage range can reach +/- 2.5 V, with an error within 30 mV (typical value 10 mV)**.

**8. Moving to PCB**

Although the circuit built on the breadboard is convenient for debugging, the phenomenon of poor contact is very serious. As long as it is touched lightly, the performance of the instrument will change. After soldering to the PCB board, a very reliable finished product will be obtained.



After drawing the schematic and PCB, produce and solder it.





At this point, the v1.0 version of an electrochemical workstation for cyclic voltammetry is complete.

SAKANA v1.0 is very easy for beginners to make, but it has a flaw: all analog power supplies are directly supplied by the Pico or DCDC switching power supply, which brings very serious power supply noise. Since the RE voltage is obtained by combining the MCP4725 output with the -6 V switching power supply output, this directly introduces about 100 mV of noise between RE/WE, superimposed with 50 Hz power line interference. This noise causes large charging and discharging currents in the electrolytic cell and may interfere with the measured electrochemical behavior. For this reason, we need to improve further.

**9. SAKANA v2.0: Further Improvements to Reduce Noise**

To further improve the noise problem, two low-noise LDOs can be used. The regulated output of the LDO is used for the power supply of all subsequent analog circuits. GM1204 and GM1206 from Common Mode Semiconductor are inexpensive and can maintain extremely high ripple rejection at frequencies up to MHz. In SAKANA v2.0, the output from the DCDC first passes through the common mode choke L1, and then is input to two LDOs respectively, converting +6/-6 V to +5/-5 V for the power supply of Op-Amps, MCP4725, INA219, and ADS1115. The -5 V regulated output is used together with the MCP4725 output to form the final potential of the RE.

In addition, since the MCP4725 actually outputs a step signal during the CV test, an RC filter is added after the output. Using Rf (10 kOhm) and C6 (0.1 uF) constitutes a filter with a time constant of about 1 ms, which to a certain extent smoothes the step signal and reduces the impact of overshoot. Care must be taken that the time constant of the filter here cannot be too large: although CV requires a triangular wave as smooth as possible, DPV requires sharp pulse signals with a duration of tens of ms. Therefore, the value here needs to balance the needs of CV and DPV. Using this version of the circuit, measuring with an oscilloscope at the RE terminal and GND of the PCB, the noise can be reduced to about 5 mV.

Since the packages of these two LDOs are very small, extra care is needed when soldering, and a hot air gun is required.





Another important source of noise is electromagnetic interference picked up from the environment by the wires extending from the PCB, of which the connection wire from RE to the electrode is the most important. In fact, if an oscilloscope is used to measure the output waveform, the significant impact of environmental interference will be clearly felt: if a wiring spring is used, the noise is only about 5 mV; but if alligator clips are used to connect the PCB and the oscilloscope, the noise will soar to more than 20 mV. This is because any wire loop in the air will pick up electromagnetic interference from the air at all times. Therefore, even if the RE/WE potential is accurate and stable on the PCB, once connected to the external electrolytic cell with ordinary wires, additional noise will be introduced. For this reason, the method of using 3 wires to connect the electrodes was changed to using aviation plugs + shielded wires. The shielded wire uses easily available 4-core shielded wire, using only 3 of them. The outer copper shielding layer is connected to the metal aviation plug, and then grounded with a wire on the aviation plug socket. At the other end of the shielded wire, 3 alligator clips are manually soldered to connect the electrodes, keeping the wires exposed outside the shielded wire as short as possible. Using this method, the final output RE/GND potential noise can be controlled within 10 mV.

Note during testing: Do not connect the oscilloscope directly across RE/WE, otherwise it will greatly change the output waveform and cause severe oscillation. To measure the potential of both, you need to measure the RE/GND potential, that is, one end of the oscilloscope connects to RE, and the other end connects to a ground point on the PCB.

In addition, to adapt to the +/- 5 V power supply, the values of each resistor were redesigned, allowing the supported potential range to reach +/- 2.8 V. The relays used to control the range were reduced to 1, corresponding to currents of the hundred uA/1 uA level respectively.

The following are photos of the actual SAKANA v2.0. The lower computer firmware uses version v2.0, and the upper computer control software is exactly the same.





With SAKANA Controller, CV, LSV, IT, and DPV can be measured. The following is an example of DPV measurement of ferricyanide in KCl aqueous solution:



**About**

The name of this project is SAKANA, which sounds similar to Cyclic.

Readers are highly encouraged to use the content introduced in this article for their own teaching and research. Anyone quoting this article must indicate the source. **Anyone publishing or conducting secondary development based on this project must cite the Github page. Commercial use without the author's consent is prohibited.**

*BSJ INSTRUMENT*

January 15, 2025

图片

This project uses results from the following Github repositories:

[chrisb2/pyb_ina219: This library for MicroPython makes it easy to leverage the complex functionality of the Texas Instruments INA219 sensor to measure voltage, current and power.](https://github.com/chrisb2/pyb_ina219)

[robert-hh/ads1x15: Micropython driver for ADS1115 and ADS1015](https://github.com/robert-hh/ads1x15)

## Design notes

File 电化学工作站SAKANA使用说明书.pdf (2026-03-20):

# 电化学工作站SAKANA使用说明书

## 物品清单

机器盒 尺寸约11 cm *11 cm *5 cm

3根母头鳄鱼夹

1个串口转USB接头（CH340），已经与机器相连。

1个Type-C或Micropython电源线（以下简称电源线）

机器盒前侧面，有电源线插头的一侧，伸出两根串口线，与CH340已经预先接好。

机器盒另一侧面处，有3根电极线，对应参比电极（RE）、工作电极（WE）、对电极（CE），可 通过鳄鱼夹与电极相连。

## 典型参数

电压范围：-2.8 V ~ +2.8 V

电压误差范围：±10 mV

最大电流：800 uA (Range 1); 8 uA (Range 2)

电流采样精度：12位

已实现方法：CV， LSV, DPV, I-t

## 使用方法

1. 在电脑上安装CH340驱动。下载地址：www.wch.cn/download/CH341SER_EXE.html
2. 在电脑上下载最新控制软件。软件下载地址：
github.com/RimoAccelerator/SAKANA/releases/tag/Windows

注意：

本软件需要.NET Framework 8或更高版本；

如果你使用笔记本电脑，为了流畅运行软件，请给笔记本接上电源。

3. 将CH340插入电脑USB口，此时CH340红灯亮起。如果使用了USB扩展坞，请注意有的扩展坞 容易松动，此时可以多换几个插口。

CH340与机器的连线方法： 如果连线不幸断开，可将两根串口线分别接到CH340的RX和TX两 个引脚。如果没有做过标记，区分两根线的方法为：打开机器盒顶盖，在PCB板上标有RX的 线，接在CH340的TX引脚；在PCB板上标有TX的线，接在CH340的RX引脚。当然也可以随机 连接，如果连接错误，在软件上点击Connect后能成功识别，但在校准、测量等操作时没有 反应，此时只需对换两根线即可。

4. 使用电源线给机器供电。电源电压为5 V，可以插在电脑的USB接头上，也可以插在手机USB 充电器上。机器预先烧录了Micropython代码，上电后会听到“啪”的一声，是继电器启动的正 常声音。如果打开盒子，会发现盒内树莓派Pico亮黄灯，盒内4个继电器中有2个亮蓝灯，说 明正常开启。
5. 运行控制软件。在COM列表中列出了检测到连接的所有串口设备。如果将电源线也连接到了 电脑，则至少有电源线、CH340这两个；如果电脑上有其他设备，列表中的可能还有更多。 可以依次选择每个设备，点击Connect、Calibration。如果能够正常进行校准，则表明这个设 备对应电化学工作站。否则，可能会在点击Connect后弹出对话框报错，也可能点击校准没 反应。

一般情况下，如果始终插在同一个USB口，设备编号就不会再变动。因此在第一次尝试找到 设备后，下次可以优先尝试连接相同编号的设备。

点击Refresh，可以刷新串口设备的列表，需注意点击Refresh后连接会断开，需要重新选择设 备并点击Connect连接。

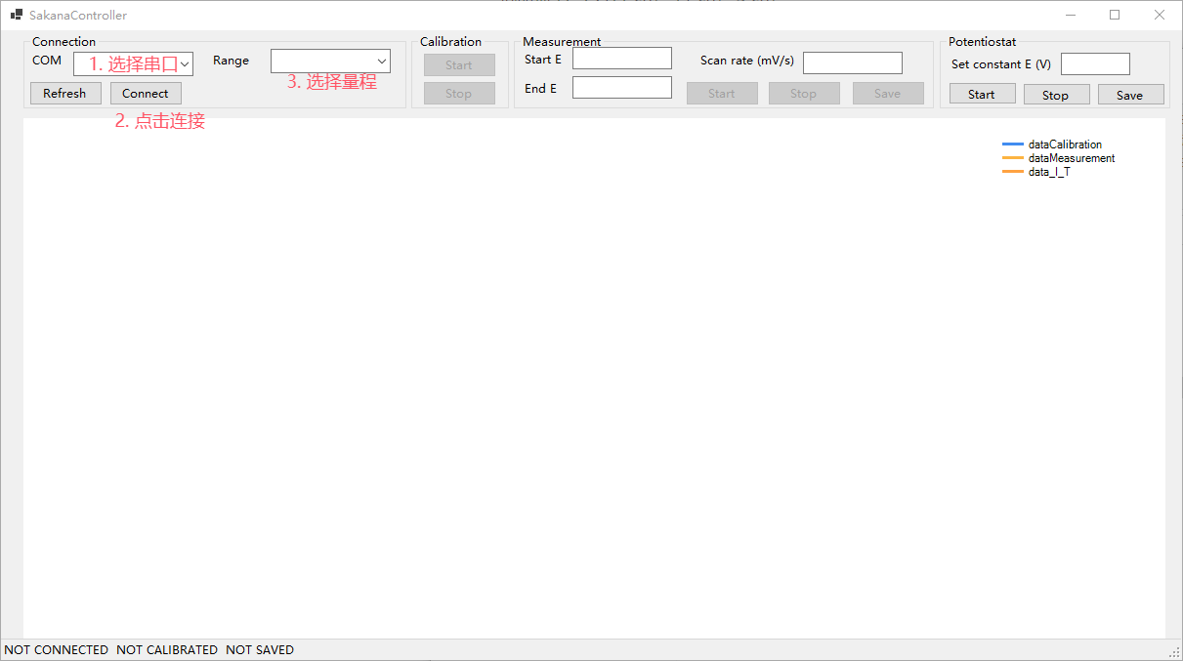
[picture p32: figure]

在Range列表处，可以选择量程，提供了100 uA, 10 uA, 1 uA三个选项，实际分别能测到800 uA, 80 uA, 8 uA左右。超过最大电流时，度数会“饱和”在某个最大值处。

默认量程为100 uA。手动更改量程时，会听到继电器切换声，说明更改成功。

6. 完成连接后，在Calibration区域，点击Start进行电压校准。

注：每次机器启动时，第一次开始校准时如果发现卡顿，可以点击Stop后再Start一次，校准 曲线就会流畅地显示出来。

校准时一定要连接电极，或将RE和CE连在一起。 正常的校准图线是一条几乎没有波动的直 线。如果发现波动，往往是由于机器与电极没接牢。 母头鳄鱼夹有时虽然看似能插紧，但实 际连接不佳，可以使用双头鳄鱼夹代替。

在观察到正常的校准图线后，可以随时点击Stop停止校准。也可以等待机器自动完成。随后 会弹出对话框，点击确定，即可进行后续操作。

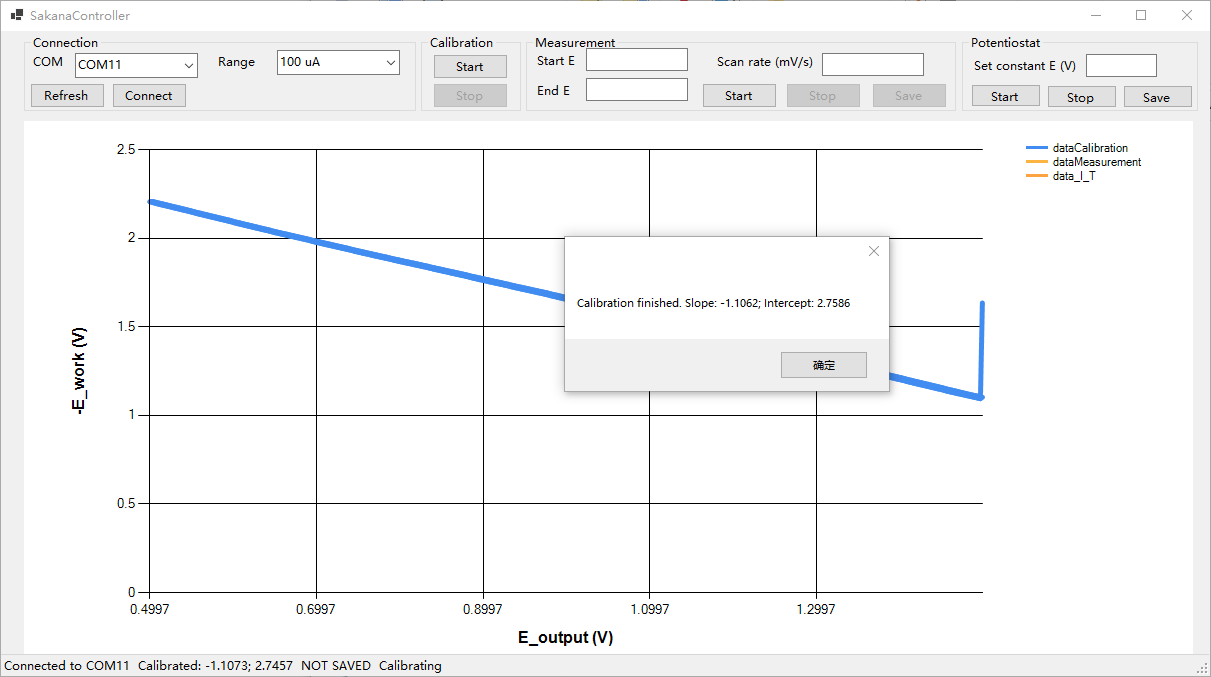
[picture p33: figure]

7. 恒电位模式

在Potentiostat区域，输入电压（对应WE相对于RE的电压），进入恒电位电解模式，同步显 示I-t曲线。在曲线开始处，电流有一段快速上升和震荡区，这是由于存在双电层和机器电容 的充电电流。可以随时点击Stop停止记录。点击Save，可以将图线保存成.txt文件。

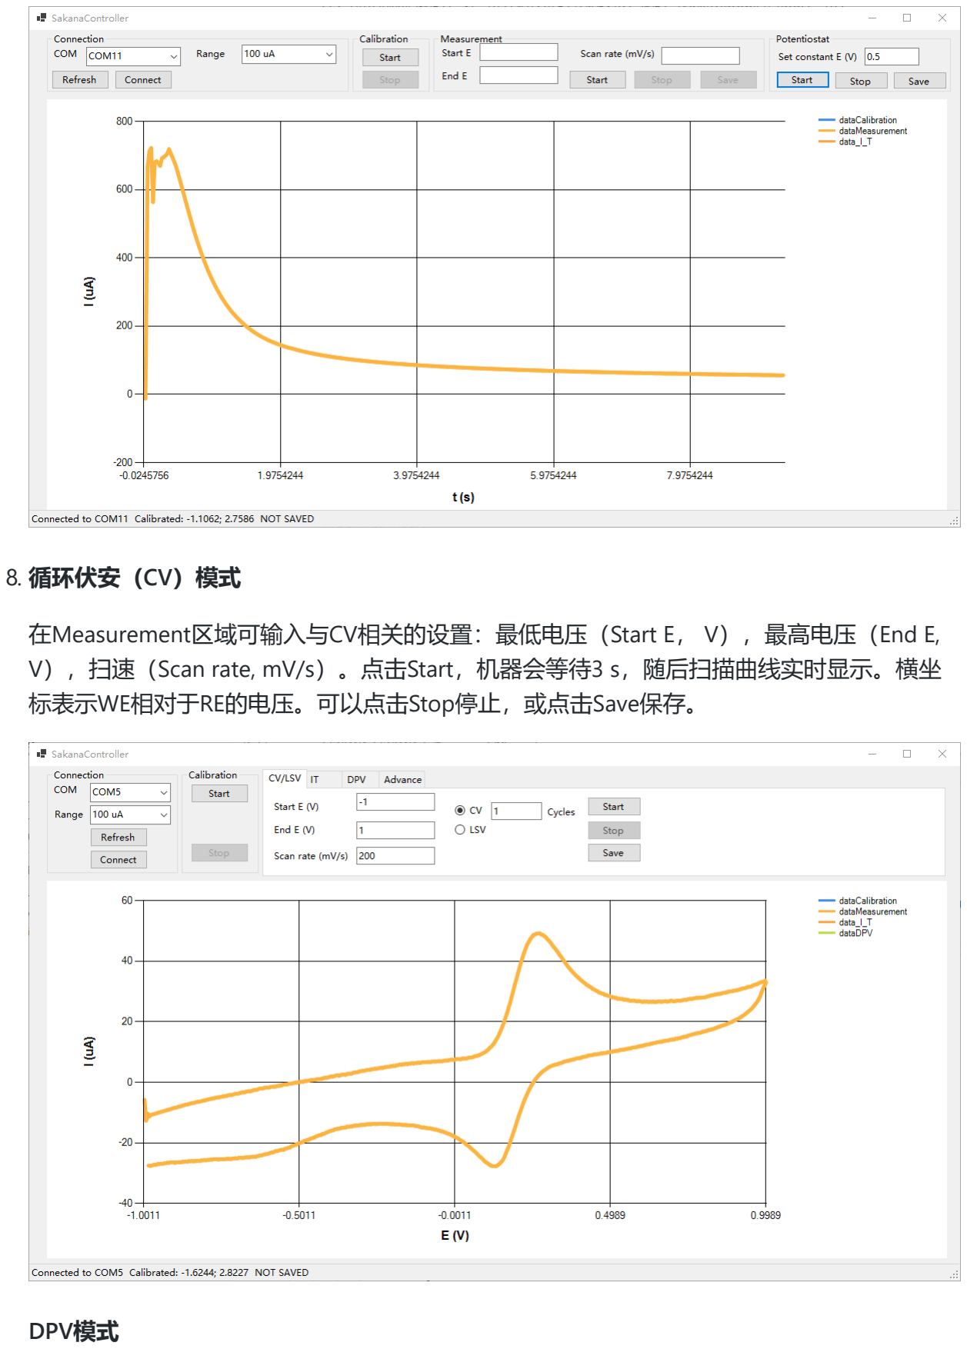
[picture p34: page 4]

8. 循环伏安（CV）模式

在Measurement区域可输入与CV相关的设置：最低电压（Start E， V），最高电压（End E, V），扫速（Scan rate, mV/s）。点击Start，机器会等待3 s，随后扫描曲线实时显示。横坐 标表示WE相对于RE的电压。可以点击Stop停止，或点击Save保存。

DPV模式

9. 在DPV区域可输入与CV相关的设置：最低电压（Start E， V），最高电压（End E, V）， 脉冲幅度（Pulse magnitude），脉冲宽度（Pulse width），采样宽度（Sampling width），步长（Increment），周期（Period）。点击Start，机器会等待2 s，随后DPV 曲线实时显示。横坐标表示WE相对于RE的电压。可以点击Stop停止，或点击Save保 存。

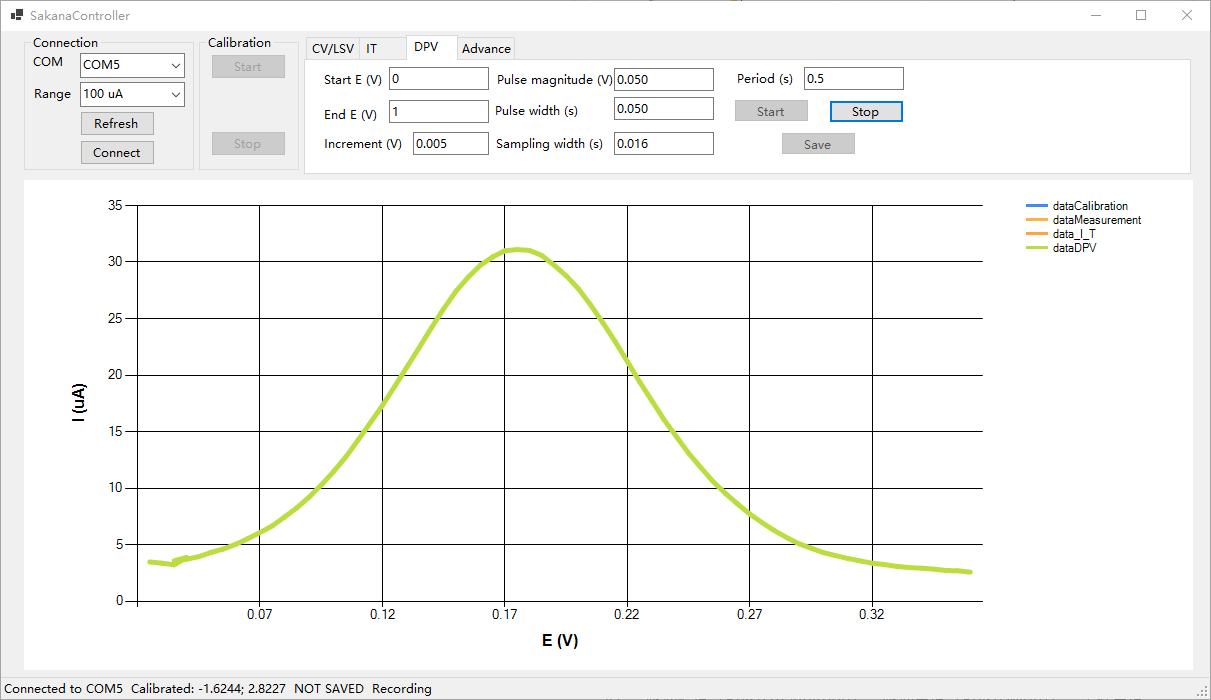
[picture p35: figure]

## 固件升级

SAKANA的控制软件和固件都可能会不断升级改进。控制软件很容易在电脑上安装，而当需要升 级固件时，可采用如下方法：

1. 下载安装VS Code: https://code.visualstudio.com/
2. 打开VS Code，选择File -> Open Folder，打开存放最新main.py的目录。
3. 在左侧点击Extensions，输入raspberry pi pico，找到raspberry pi pico扩展并安装。

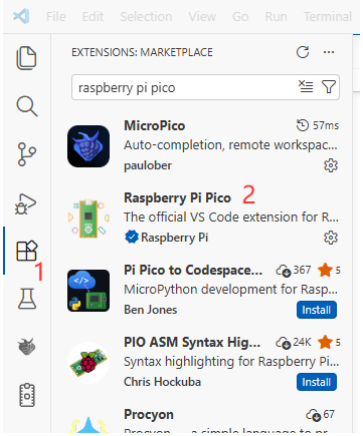
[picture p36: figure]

4. 安装完成后，插入Type-C线（注意这里不是先插入串口线）。这时界面底部终端应该会识别 出设备：
5. 打开main.py，然后在左侧文件管理器里找到main.py，右键点击，选择Upload File to Pico。 等待传输完成，关闭VS Code，拔下连接线，然后按照正常方法使用即可。

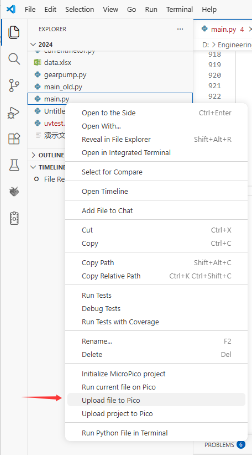
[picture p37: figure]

## 针对开发人员

如果你希望对SAKANA进行二次开发，以下内容可能有用。

### 串口通信格式

不使用控制软件时，也可以通过串口发送指令的方式控制SAKANA，波特率为115200。以下是当 前支持的串口命令（#后的是注释）：

cali #开始电压校准
stopcali #停止电压校准
stopmeas #停止CV测量
stopit #停止恒电位测量
par xxx yyy #设置电压校准参数，xxx和yyy分别是电压校准得到的斜率和截距 set xxx #开始恒电位模式，xxx是电压数值
measure v_start v_end scan_rate #开始CV测量
range 0 #设置量程为100 uA
range 1 #设置量程为10 uA
range 2 #设置量程为1 uAn
numcyc N #设置CV扫描圈数。N = 0时对应LSV。

串口返回值如下，所有返回信号都以$开头，以%结尾：

$fini% #校准/测量完成
$xxx yyy% #如果在校准模式，则xxx为MCP4725的输出电压，yyy为RE相对于地的电压
#如果在CV模式，则xxx和yyy分别为此时WE的电压和电流

$xxx% #恒电位模式下，以此格式返回当前时刻的电流值

### 电压/电流手动校准

在内置的固件程序中，已经对作为电压/电流测量模块的ADS1115和INA219进行了一般性的校 准。如果你追求更高精度，可以针对每台机器分别进行校准。方法如下：

20260320更新后电压/电流校准变得非常简便，可以在最新版SakanaController中图形化操作。注 意必须使用20260320更新的固件。

电压校准

1. 打开Advanced选项卡，此处记录了当前的当前的校准系数。它描述的是真实电压/电流与内 部传感器直接采集的电压/电流的线性关系。
2. 点击Reset，斜率变成1，截距变成0. 将RE和CE连接，用高精度万用表或示波器连接RE和PCB 上的接地孔位（在航空插头旁边）。在控制软件中，完成电压校准后，利用恒电位模式，输 入电压数值，记录仪表读取到的实际电压数值。测定若干组后，进行线性回归，将斜率和截 距重新填写进文本框。

电流校准

在完成电压校准后，将RE和CE连接，用一个精确已知阻值的电阻将CE和WE连接。在电流校准 斜率和截距分别为1和0的情况下，利用I-t功能指定电压，进行电流测量，并与根据欧姆定律所得 的预期值对照。测定若干组后，进行线性回归，将斜率和截距替换进文本框中。

在完成全部校准后，点击Write，相关系数及被写入机器。

最后，感谢你对本项目的支持。使用过程中如遇到问题，请向开发者反馈。我们所做的工作，将 会为更普及、更便捷和更自由的科学研究贡献一份力量。

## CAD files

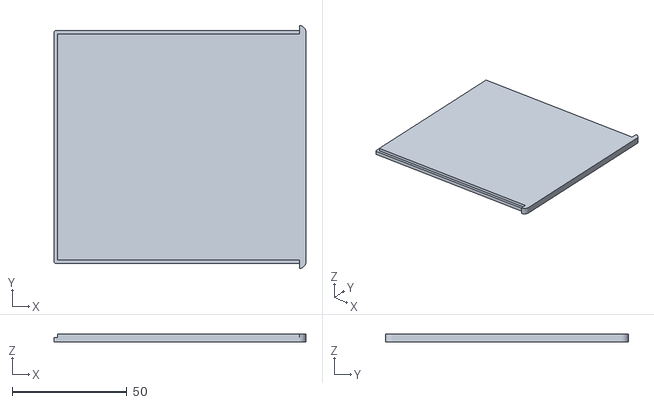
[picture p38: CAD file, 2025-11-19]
Hardware/v2.0/Shell_V2/3DShell_3DShell_PCB1_4_T.stl
109.9 x 106.0 x 3.60

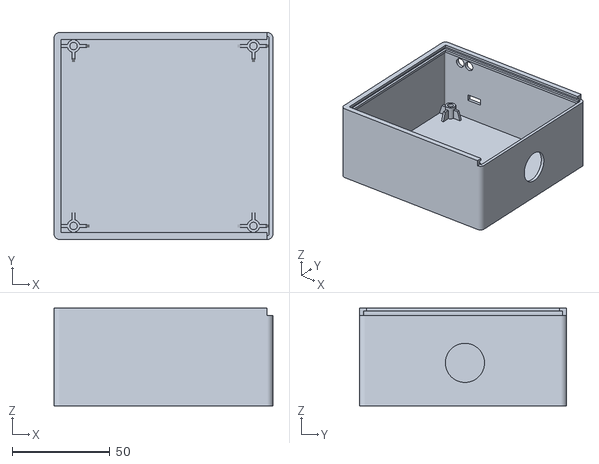
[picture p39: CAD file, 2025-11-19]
Hardware/v2.0/Shell_V2/3DShell_3DShell_PCB1_4_B.stl
112.0 x 106.0 x 50.0

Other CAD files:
Hardware/v1.0/Shell/3DShell_3DShell_PCB1_T.stl
Hardware/v1.0/Shell/3DShell_3DShell_PCB1_B.stl

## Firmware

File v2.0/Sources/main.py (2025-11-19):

# https://github.com/chrisb2/pyb_ina219
"""MicroPython library for the INA219 sensor.
This library supports the INA219 sensor from Texas Instruments with
MicroPython using the I2C bus.
"""
#import logging
import utime
from math import trunc
from micropython import const

# https://github.com/chrisb2/pyb_ina219
class INA219:
    """Provides all the functionality to interact with the INA219 sensor."""

    RANGE_16V = const(0)  # Range 0-16 volts
    RANGE_32V = const(1)  # Range 0-32 volts

    GAIN_1_40MV = const(0)  # Maximum shunt voltage 40mV
    GAIN_2_80MV = const(1)  # Maximum shunt voltage 80mV
    GAIN_4_160MV = const(2)  # Maximum shunt voltage 160mV
    GAIN_8_320MV = const(3)  # Maximum shunt voltage 320mV
    GAIN_AUTO = const(-1)  # Determine gain automatically

    ADC_9BIT = const(0)  # 9-bit conversion time  84us.
    ADC_10BIT = const(1)  # 10-bit conversion time 148us.
    ADC_11BIT = const(2)  # 11-bit conversion time 2766us.
    ADC_12BIT = const(3)  # 12-bit conversion time 532us.
    ADC_2SAMP = const(9)  # 2 samples at 12-bit, conversion time 1.06ms.
    ADC_4SAMP = const(10)  # 4 samples at 12-bit, conversion time 2.13ms.
    ADC_8SAMP = const(11)  # 8 samples at 12-bit, conversion time 4.26ms.
    ADC_16SAMP = const(12)  # 16 samples at 12-bit,conversion time 8.51ms
    ADC_32SAMP = const(13)  # 32 samples at 12-bit, conversion time 17.02ms.
    ADC_64SAMP = const(14)  # 64 samples at 12-bit, conversion time 34.05ms.
    ADC_128SAMP = const(15)  # 128 samples at 12-bit, conversion time 68.10ms.

    __ADC_CONVERSION = {
        ADC_9BIT: "9-bit",
        ADC_10BIT: "10-bit",
        ADC_11BIT: "11-bit",
        ADC_12BIT: "12-bit",
        ADC_2SAMP: "12-bit, 2 samples",
        ADC_4SAMP: "12-bit, 4 samples",
        ADC_8SAMP: "12-bit, 8 samples",
        ADC_16SAMP: "12-bit, 16 samples",
        ADC_32SAMP: "12-bit, 32 samples",
        ADC_64SAMP: "12-bit, 64 samples",
        ADC_128SAMP: "12-bit, 128 samples"
    }

    __ADDRESS = 0x40

    __REG_CONFIG = 0x00
    __REG_SHUNTVOLTAGE = 0x01
    __REG_BUSVOLTAGE = 0x02
    __REG_POWER = 0x03
    __REG_CURRENT = 0x04
    __REG_CALIBRATION = 0x05

    __RST = 15
    __BRNG = 13
    __PG1 = 12
    __PG0 = 11
    __BADC4 = 10
    __BADC3 = 9
    __BADC2 = 8
    __BADC1 = 7
    __SADC4 = 6
    __SADC3 = 5
    __SADC2 = 4
    __SADC1 = 3
    __MODE3 = 2
    __MODE2 = 1
    __MODE1 = 0

    __OVF = 1
    __CNVR = 2

    __BUS_RANGE = [16, 32]
    __GAIN_VOLTS = [0.04, 0.08, 0.16, 0.32]

    __CONT_SH_BUS = 7

    __AMP_ERR_MSG = ('Expected current %.3fA is greater '
                     'than max possible current %.3fA')
    __RNG_ERR_MSG = ('Expected amps %.2fA, out of range, use a lower '
                     'value shunt resistor')
    __VOLT_ERR_MSG = ('Invalid voltage range, must be one of: '
                      'RANGE_16V, RANGE_32V')

    __LOG_FORMAT = '%(asctime)s - %(levelname)s - INA219 %(message)s'
    __LOG_MSG_1 = ('shunt ohms: %.3f, bus max volts: %d, '
                   'shunt volts max: %.2f%s, '
                   'bus ADC: %s, shunt ADC: %s')
    __LOG_MSG_2 = ('calibrate called with: bus max volts: %dV, '
                   'max shunt volts: %.2fV%s')
    __LOG_MSG_3 = ('Current overflow detected - '
                   'attempting to increase gain')

    __SHUNT_MILLIVOLTS_LSB = 0.01  # 10uV
    __BUS_MILLIVOLTS_LSB = 4  # 4mV
    __CALIBRATION_FACTOR = 0.04096
    # Max value supported value (65534 decimal) of the calibration register
    # (D0 bit is always zero, p31 of spec)
    __MAX_CALIBRATION_VALUE = 0xFFFE
    # In the spec (p17) the current LSB factor for the minimum LSB is
    # documented as 32767, but a larger value (100.1% of 32767) is used
    # to guarantee that current overflow can always be detected.
    __CURRENT_LSB_FACTOR = 32800

    def __init__(self, shunt_ohms, i2c, max_expected_amps=None,
                 address=__ADDRESS):
        """Construct the class.
        At a minimum pass in the resistance of the shunt resistor and I2C
        interface to which the sensor is connected.
        Arguments:
        shunt_ohms -- value of shunt resistor in Ohms (mandatory).
        i2c -- an instance of the I2C class from the *machine* module, either
            I2C(1) or I2C(2) (mandatory).
        max_expected_amps -- the maximum expected current in Amps (optional).
        address -- the I2C address of the INA219, defaults to
            *0x40* (optional).
        log_level -- set to logging.DEBUG to see detailed calibration
            calculations (optional).
        """
        self._i2c = i2c
        self._address = address
        self._shunt_ohms = shunt_ohms
        self._max_expected_amps = max_expected_amps
        self._min_device_current_lsb = self._calculate_min_current_lsb()
        self._gain = None
        self._auto_gain_enabled = False

    def configure(self, voltage_range=RANGE_32V, gain=GAIN_AUTO,
                  bus_adc=ADC_12BIT, shunt_adc=ADC_12BIT):
        """Configure and calibrate how the INA219 will take measurements.
        Arguments:
        voltage_range -- The full scale voltage range, this is either 16V
            or 32V represented by one of the following constants;
            RANGE_16V, RANGE_32V (default).
        gain -- The gain which controls the maximum range of the shunt
            voltage represented by one of the following constants;
            GAIN_1_40MV, GAIN_2_80MV, GAIN_4_160MV,
            GAIN_8_320MV, GAIN_AUTO (default).
        bus_adc -- The bus ADC resolution (9, 10, 11, or 12-bit) or
            set the number of samples used when averaging results
            represent by one of the following constants; ADC_9BIT,
            ADC_10BIT, ADC_11BIT, ADC_12BIT (default),
            ADC_2SAMP, ADC_4SAMP, ADC_8SAMP, ADC_16SAMP,
            ADC_32SAMP, ADC_64SAMP, ADC_128SAMP
        shunt_adc -- The shunt ADC resolution (9, 10, 11, or 12-bit) or
            set the number of samples used when averaging results
            represent by one of the following constants; ADC_9BIT,
            ADC_10BIT, ADC_11BIT, ADC_12BIT (default),
            ADC_2SAMP, ADC_4SAMP, ADC_8SAMP, ADC_16SAMP,
            ADC_32SAMP, ADC_64SAMP, ADC_128SAMP
        """
        self.__validate_voltage_range(voltage_range)
        self._voltage_range = voltage_range

        if self._max_expected_amps is not None:
            if gain == self.GAIN_AUTO:
                self._auto_gain_enabled = True
                self._gain = self._determine_gain(self._max_expected_amps)
            else:
                self._gain = gain
        else:
            if gain != self.GAIN_AUTO:
                self._gain = gain
            else:
                self._auto_gain_enabled = True
                self._gain = self.GAIN_1_40MV

        self._calibrate(
            self.__BUS_RANGE[voltage_range], self.__GAIN_VOLTS[self._gain],
            self._max_expected_amps)
        self._configure(voltage_range, self._gain, bus_adc, shunt_adc)

    def voltage(self):
        """Return the bus voltage in volts."""
        value = self._voltage_register()
        return float(value) * self.__BUS_MILLIVOLTS_LSB / 1000

    def supply_voltage(self):
        """Return the bus supply voltage in volts.
        This is the sum of the bus voltage and shunt voltage. A
        DeviceRangeError exception is thrown if current overflow occurs.
        """
        return self.voltage() + (float(self.shunt_voltage()) / 1000)

    def current(self):
        """Return the bus current in milliamps.
        A DeviceRangeError exception is thrown if current overflow occurs.
        """
        self._handle_current_overflow()
        return self._current_register() * self._current_lsb * 1000

    def power(self):
        """Return the bus power consumption in milliwatts.
        A DeviceRangeError exception is thrown if current overflow occurs.
        """
        self._handle_current_overflow()
        return self._power_register() * self._power_lsb * 1000

    def shunt_voltage(self):
        """Return the shunt voltage in millivolts.
        A DeviceRangeError exception is thrown if current overflow occurs.
        """
        self._handle_current_overflow()
        return self._shunt_voltage_register() * self.__SHUNT_MILLIVOLTS_LSB

    def sleep(self):
        """Put the INA219 into power down mode."""
        configuration = self._read_configuration()
        self._configuration_register(configuration & 0xFFF8)

#    def wake(self):
#        """Wake the INA219 from power down mode."""
#        configuration = self._read_configuration()
#        self._configuration_register(configuration | 0x0007)
#        # 40us delay to recover from powerdown (p14 of spec)
#        utime.sleep_us(40)
        

    def current_overflow(self):
        """Return true if the sensor has detect current overflow.
        In this case the current and power values are invalid.
        """
        return self._has_current_overflow()

    def reset(self):
        """Reset the INA219 to its default configuration."""
        self._configuration_register(1 << self.__RST)

    def _handle_current_overflow(self):
        if self._auto_gain_enabled:
            while self._has_current_overflow():
                self._increase_gain()
        else:
            if self._has_current_overflow():
                raise DeviceRangeError(self.__GAIN_VOLTS[self._gain])

    def _determine_gain(self, max_expected_amps):
        shunt_v = max_expected_amps * self._shunt_ohms
        if shunt_v > self.__GAIN_VOLTS[3]:
            raise ValueError(self.__RNG_ERR_MSG % max_expected_amps)
        gain = min(v for v in self.__GAIN_VOLTS if v > shunt_v)
        return self.__GAIN_VOLTS.index(gain)
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

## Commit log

2025-02-13 Add capacitors for OpAmp Power Supply
2025-02-14 Pico current output during I_T mode
2025-03-28 New func: set cycle number for CV
    [3DShell_3DShell_PCB1_B.stl, 3DShell_3DShell_PCB1_T.stl]
2026-03-20 Important Update 20260320
    1. Fix wrong labels (R2 and R3) on PCB board.
    2. Cotroller updated: simplified current/voltage correction.
    3. File reorganized.
    [3DShell_3DShell_PCB1_4_B.stl, 3DShell_3DShell_PCB1_4_T.stl, 3DShell_3DShell_PCB1_B.stl, 3DShell_3DShell_PCB1_T.stl]
